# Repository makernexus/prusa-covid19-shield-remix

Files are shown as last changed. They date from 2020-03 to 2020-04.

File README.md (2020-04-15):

MakerNexus local modifications
------------------------------

At [MakerNexus], we're working on
[making as many face-shields as possible][covidshieldnexus] as possible;
They will be in dire demand very soon and we got requests of thousands of them.
MakerNexus is coordinating the contact with the local hospitals and
as well the effort of non-Members of the maker-space to 3D print. We
have enough shield material to laser-cut, but of course 3D printing is the
slow part of manufacturing.

Please check out the [project page] if you are in the San Francisco
Bay Area and want to help.

We are using the [Prusa-rc3] design, but needed some modifications requested
by the local healthcare community.

### Design goals

When reviewing, the local healthcare providers requested

   * Weight-reduce front-part if possible.
   * Move the shield pins up so that there is material behind the openings
     of the shield-punches
   * Larger radius of crevices to allow better sterilization access.

Moving up the shield-pin requires a little bit of support material, but it
is not a problem to generate the necessary STL file where the supports should
be and use that in the Prusa slicer as support modifier.

### Download

Choose what bests fits your circumstances. GCode is 'ready to go', 3mf allows
printer adjustments, *.stl allows to use in your own slicer.

You can just use the files below directly. If you want to work on the repo,
pull requests are welcome, but please discuss things first on slack.

### Release content

We are only printing the 'thin' shield version now (15mm vs. 20mm before).

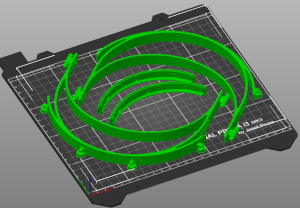
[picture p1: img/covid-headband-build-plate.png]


#### Cut to the chase: GCode ready to use

Recommended

  * For **PETG** [T9-PETG-Prusa.gcode](https://github.com/makernexus/prusa-covid19-shield-remix/raw/v1.9/fab/T9-PETG-Prusa.gcode) (right click, download or *save link as...*) GCode file placing 2 head-bands on build-plate. Ready to go on Prusa MK3(s) with 0.3mm layer, 100% infill, 240°C temp for PETG printing. This prints two thin bands which is faster to print and works fine with PETG.

  * For **PLA** [T9-PLA-Prusa.gcode](https://github.com/makernexus/prusa-covid19-shield-remix/raw/v1.9/fab/T9-PLA-Prusa.gcode) (right click, download or *save link as...*) Same for PLA. Currently this is the regular sized band as we still need to test if the thinner band will work with PLA.

The resulting headband has a version imprint on one temple with a letter
denoting `T` = thin band, and `s` = stacked, followed a version number.



#### More files

 * [thin_shield_with_support.stl](https://github.com/makernexus/prusa-covid19-shield-remix/raw/v1.9/fab/thin_shield_with_support.stl) and
   [thin_shield_no_support.stl](https://github.com/makernexus/prusa-covid19-shield-remix/raw/v1.9/fab/thin_shield_no_support.stl). The *with_support* version has already a support column included
   for printing the pin. Make sure you have **thin wall detection** enabled in
   your slicer. If you choose the *no support* version, you need
   to use your slicer to create support for the mounting pins.

If you have checked out code from github, you might need to first `make` it
and reload the STLs in the 3mf. The STLs and 3mf are usually only updated in
git for a new release (click on the stl in the list on the right in prusa slicer
and say 'reload from disk').

#### Stacked arrangement
There are 3mf's for stacks and makefile-rules to create various height stack
arrangements. The 3mf's with 'FAST' in their name are tweaked for very fast
prints, but it requires some tweaking depending on your filament to get the
flow-rate right and the separability correct. For details about the speed
improvements see the [Fast-Stacks](./Fast-Stacks.txt) documentation.

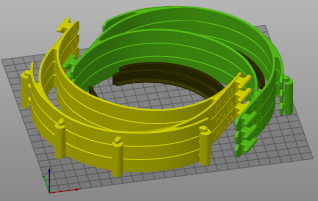
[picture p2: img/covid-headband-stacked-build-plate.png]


The way these stacks work is that they have a one-layer gap between them, with
the intent to have a weak layer adhesion there to be able to separate, but
still strong enough to print the next layers. This is the reason why it also
requires some tweaking which is very dependent on the printer and filament you
have, so we don't distribute any GCode. The gap height is 0.25mm, so this is
the layer thickness needed in your slicer (or modify the `print_layer_height`
in the Makefile).

If you use a different slicer than Prusa slicer, you can also create STLs for
the stacks and slice these.

```shell
make fab/thin-stack3.stl
```

### Faceshield

The face-shield has been optimized at MakerNexus to meet the needs of the
healthcare workers to be also protected above the headband. You find the
[maker-nexus-faceshield-cut.svg file](./baseline/maker-nexus-faceshield-cut.svg)
and [maker-nexus-faceshield-cut.dxf](./baseline/maker-nexus-faceshield-cut.dxf)
in the [baseline/](./baseline) subdirectory

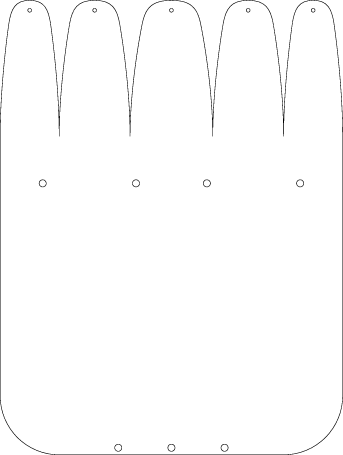
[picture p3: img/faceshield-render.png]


### Code

A simple OpenSCAD file that take the original STL and does the necessary
surgical changes.

### Slicer project file
A 3mf file is provided, so it can be loaded into slicer right away:

```
git clone https://github.com/hzeller/prusa-covid19-shield-remix.git
cd prusa-covid19-shield-remix
prusa-slicer thin_shield.3mf
```

### Replication Script

A script is provided that will take an existing Prusa Slicer project file (.3mf) with a single model already imported and fill the bed with as many of that model that will fit.  The script must be run with the python3 interpreter:

```
python3 scripts/replicate_model.py --help
usage: replicate_model.py [-h] [-w BED_WIDTH] [-d BED_DEPTH] -m MODEL -o
                          OUTPUT [--x_offset X_OFFSET] [--y_offset Y_OFFSET]
                          [--left_offset LEFT_OFFSET]
                          [--right_offset RIGHT_OFFSET]
                          [--front_offset FRONT_OFFSET]
                          [--rear_offset REAR_OFFSET] [-x X_SPACING]
                          [-X X_GAP] [-y Y_SPACING] [-Y Y_GAP]

optional arguments:
  -h, --help            show this help message and exit
  -w BED_WIDTH, --bed_width BED_WIDTH
                        Width of the print bed in mm (default: 250)
  -d BED_DEPTH, --bed_depth BED_DEPTH
                        Depth of the print bed in mm (default: 210)

required options:
  -m MODEL, --model MODEL
                        Baseline .3mf model file with one instance of the
                        model to be duplicated
  -o OUTPUT, --output OUTPUT
                        Output .3mf model file with one instance of the model
                        to be duplicated

keepout options:
  --x_offset X_OFFSET   X-axis offset from left and right edges of the bed
  --y_offset Y_OFFSET   Y-axis offset from front and rear edges of the bed
  --left_offset LEFT_OFFSET
                        Offset from the left side of the bed (x-axis, left
                        side only)
  --right_offset RIGHT_OFFSET
                        Offset from the right side of the bed (x-axis, right
                        side only)
  --front_offset FRONT_OFFSET
                        Offset from the front of the bed (y-axis, front only)
  --rear_offset REAR_OFFSET
                        Offset from the back of bed (y-axis, back only)

layout options:
  -x X_SPACING, --x_spacing X_SPACING
                        X-axis spacing in mm from the start of one instance of
                        the model to the next. This allows the models to
                        overlap in the X-axis.
  -X X_GAP, --x_gap X_GAP
                        X-axis gap from the edge of one model to the next
  -y Y_SPACING, --y_spacing Y_SPACING
                        Y-axis spacing in mm from the start of one instance of
                        the model to the next. This allows the models to
                        overlap in the Y-axis.
  -Y Y_GAP, --y_gap Y_GAP
                        Y-axis gap from the edge of one model to the next
```

There are only two required options (-m <source model> and -o <output model>).  The rest control the location on the bed / keepout areas where the objects can be laid out and then control the replication process itself.

All measurements are specified in mm and can be decimal values (e.g. 5.4).

The objects will be laid out in a grid pattern in rows and columns.  For the layout options, there are two ways the layout will be performed.  If the spacing options is specified, the object will be replicated at the given interval (e.g. every 10mm in the specified axis).  This allows each model to overlap the previous one.  If spacing is not provided, then the gap value will be used and the objects will have the specified gap between them.

With the specified bed dimensions, keepout area and layout options, the script will fit as many of the object as possible in the allowed area.

For the bottom support with the open curve facing downwards, it is desirable to have a gap in the X-axis, but to provide a spacing for the Y-axis.  The Makefile uses the following options to produce a dense, printable layout for the Prusa i3 mk3:

```
python3 scripts/replicate_model.py \
--model baseline/bottom_reinforcement-single-fast.3mf \
--output fab/bottom_reinforcement-full_plate-fast.3mf \
--x_offset 4 --front_offset 10 --x_gap 1 --y_spacing 8.2
```

With those options, the project file 'baseline/bottom\_reinforcement-single-fast.3ml' will be read and the first model replicated per the keepout/layout options.  It will then be written into the output project file 'fab/bottom\_reinforcement-full\_plate-fast.3mf'.

The default bed size (250 x 210) will be used with 4mm of space on the left and right side and 10mm of space on the bottom and 5mm on top.  (I have added more space to the bottom for the mk3 as the bottom corners aren't heated as well and the model may warp and get knocked off of the bed in those locations).  When laying out the replicated model, it will keep a 1mm gap between the columns and lay out the model vertically every 8.2mm.  That leaves enough gap between each so that the separate instances don't join together when printed.

This is what the output looks like:

```
python3 scripts/replicate_model.py --model baseline/bottom_reinforcement-single-fast.3mf --output fab/bottom_reinforcement-full_plate-fast.3mf --x_offset 4 --front_offset 10 --rear_offset 5 --x_gap 1 --y_spacing 8.2
replicate_model: Bed dimensions: [250 x 210]
replicate_model: Bed keep-out:
replicate_model:                 Rear: 5.0
replicate_model:           -----------------------
replicate_model:           |                     |
replicate_model: Left: 4.0 |                     | Right: 4.0
replicate_model:           |                     |
replicate_model:           -----------------------
replicate_model:                 Front: 10.0
replicate_model:
replicate_model: Processing project file (.3mf): baseline/bottom_reinforcement-single-fast.3mf
replicate_model: Model dimensions: [120.0572968 x 30.5739136]
replicate_model: Printing 42 objects [2 x 21]
replicate_model: Output project file (.3mf): fab/bottom_reinforcement-full_plate-fast.3mf
replicate_model: Complete.
```

### GCode
There is also gcode directly sliced for Prusa MK3(s). See above.

### Development

For building, use the Makefile to create all the artifacts from the *.scad
file

```
make
```

### License

License: [CC-BY-NC]

This is based on the Prusa design
https://www.prusaprinters.org/prints/25857-prusa-protective-face-shield-rc2

[MakerNexus]: https://www.makernexus.com/
[covidshieldnexus]: https://www.covidshieldnexus.org/
[prusa-rc3]: https://www.prusaprinters.org/prints/25857-prusa-protective-face-shield-rc3
[CC-BY-NC]: https://creativecommons.org/licenses/by-nc/4.0/
[project page]: http://makernexuswiki.com/index.php?title=3D_printed_face_shields
[prusa-slicer]: https://www.prusa3d.com/prusaslicer/

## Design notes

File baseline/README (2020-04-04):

All Licenses for these files: CC-BY-NC

The baseline STL we were starting out with.
https://www.prusaprinters.org/prints/25857-prusa-protective-face-shield-rc2

The RC2-nexusized files are made by Rich Rauenzahn, using a CAD model
provided by Adafruit This includes changes based on feedback from our
healthcare providers.

Adafruit tutorial: http://youtube.com/watch?v=BYPWB5-auQE

The maker-nexus-faceshield-cut.svg is the laser cutting instruction for the
faceshield. It has the MakerNexus improvements in coordination with the local
healthcare providers, protecting above the head.
maker-nexus-faceshield-cut.dxf is a DXF version of the same thing (it is
created by the Makefile one level up, but checked in here for convenience).

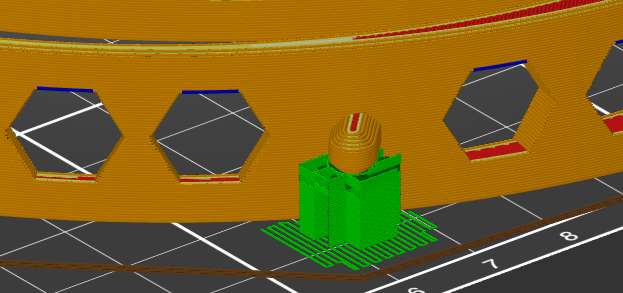
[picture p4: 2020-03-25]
img/minimal-support.png

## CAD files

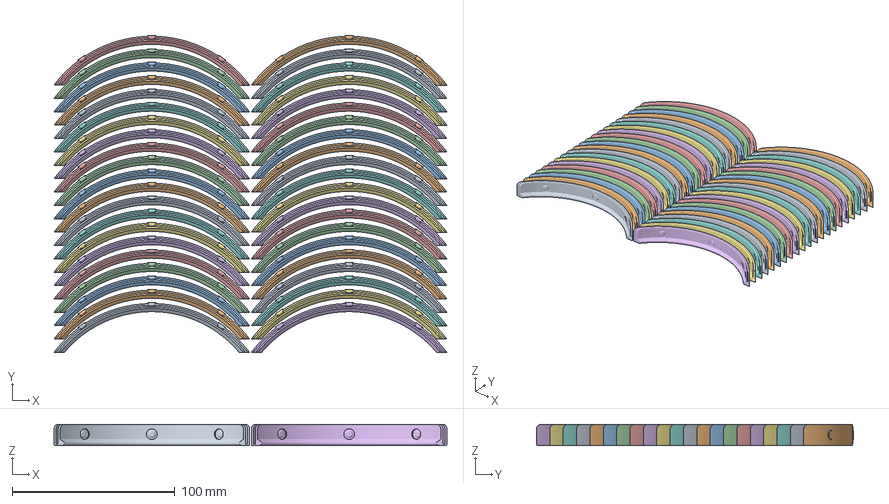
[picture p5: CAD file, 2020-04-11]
fab/bottom_reinforcement-full_plate-fast.3mf
241.1 x 194.6 x 13.0 mm

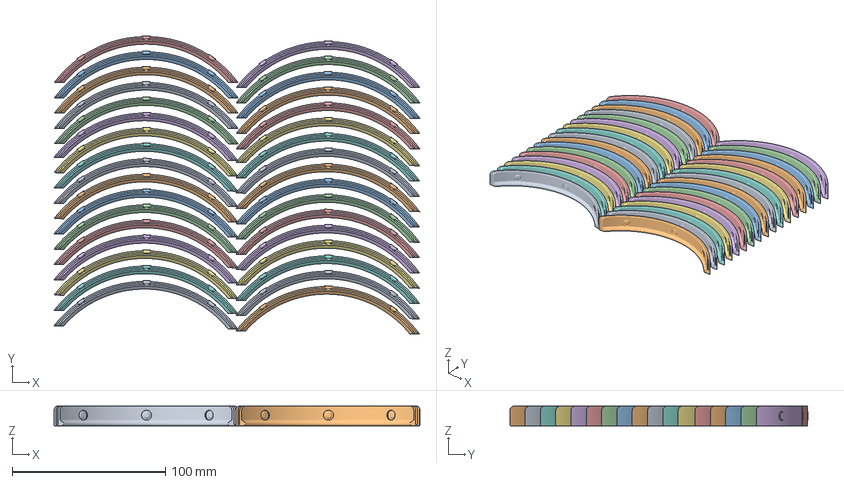
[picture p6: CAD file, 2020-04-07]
plate-full-of-bottom-supports.3mf
239.1 x 195.0 x 13.0 mm
bottom_reinforcement.stl x 2

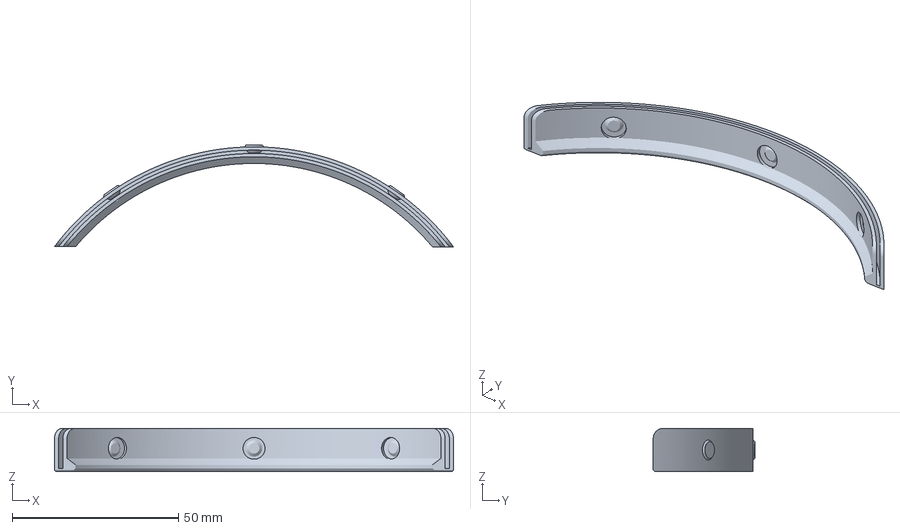
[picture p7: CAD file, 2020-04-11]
baseline/bottom_reinforcement-single-fast.3mf
120.1 x 30.6 x 13.0 mm

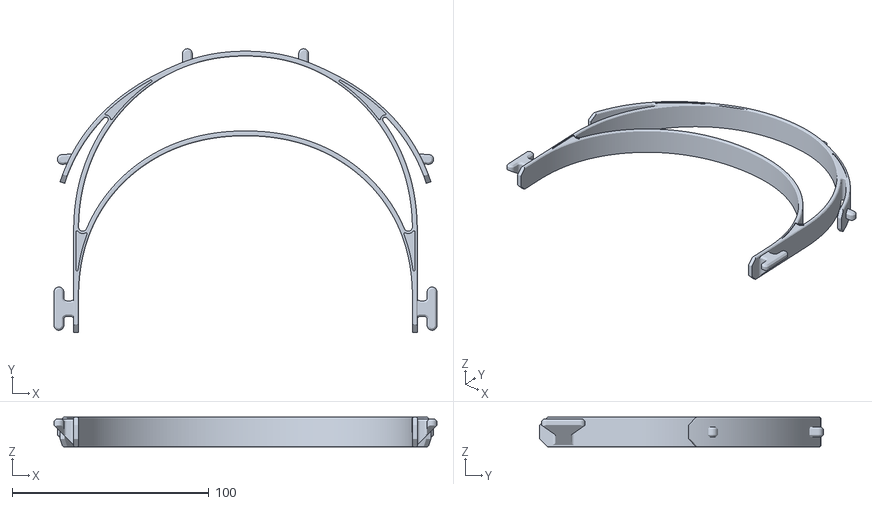
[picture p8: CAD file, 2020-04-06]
baseline/RC2-nexusized-thin-pla.stl
194.5 x 144.0 x 15.0

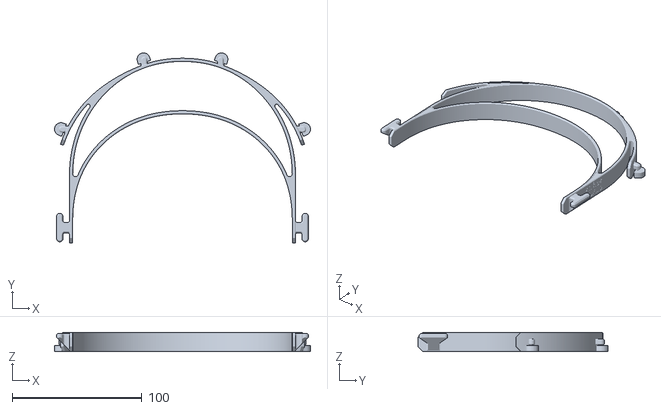
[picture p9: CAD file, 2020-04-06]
fab/thin_shield_with_support.stl
197.6 x 146.9 x 15.0

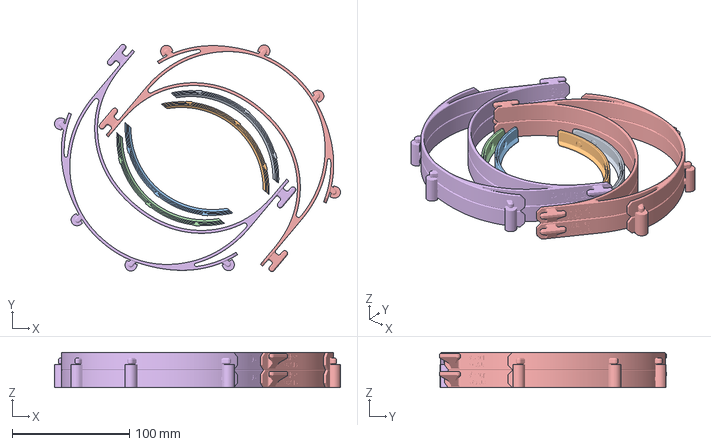
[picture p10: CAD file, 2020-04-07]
thin-shield-4stack_2x2-FAST.3mf
244.4 x 194.3 x 30.2 mm
bottom_reinforcement.stl
thin-stack2.stl

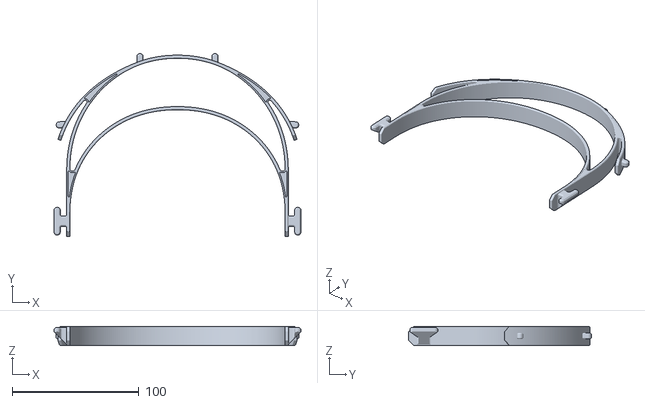
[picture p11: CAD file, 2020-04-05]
baseline/RC2-nexusized-thin.stl
194.5 x 144.0 x 15.0

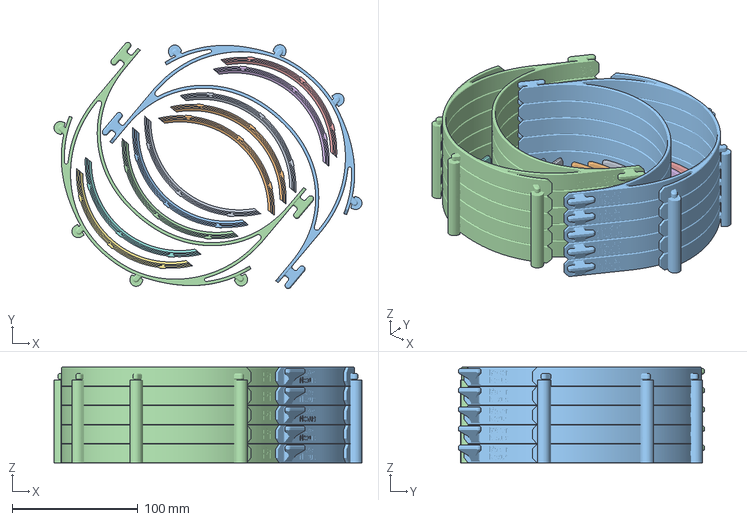
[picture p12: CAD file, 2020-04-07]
thin-shield-10stack_2x5-FAST.3mf
244.6 x 195.6 x 76.0 mm
bottom_reinforcement.stl
thin-stack5.stl

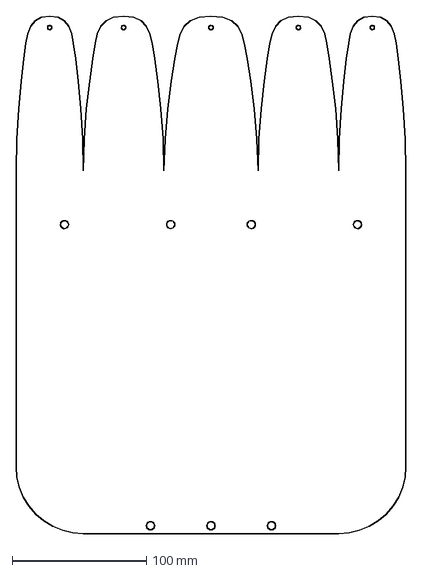
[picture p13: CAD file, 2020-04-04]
baseline/maker-nexus-faceshield-cut.dxf
290.0 x 385.0 mm

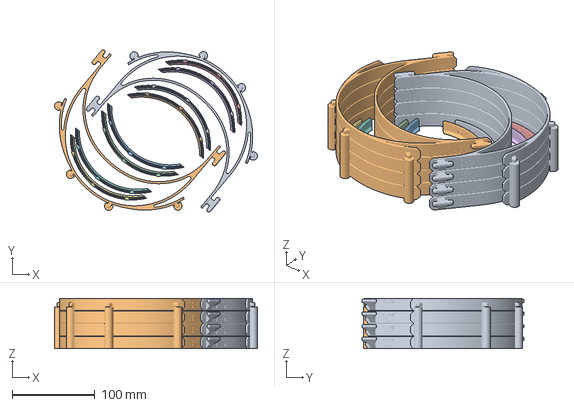
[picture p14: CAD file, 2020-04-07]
thin-shield-8stack_2x4-FAST.3mf
244.7 x 195.8 x 60.8 mm
bottom_reinforcement.stl
thin-stack4.stl

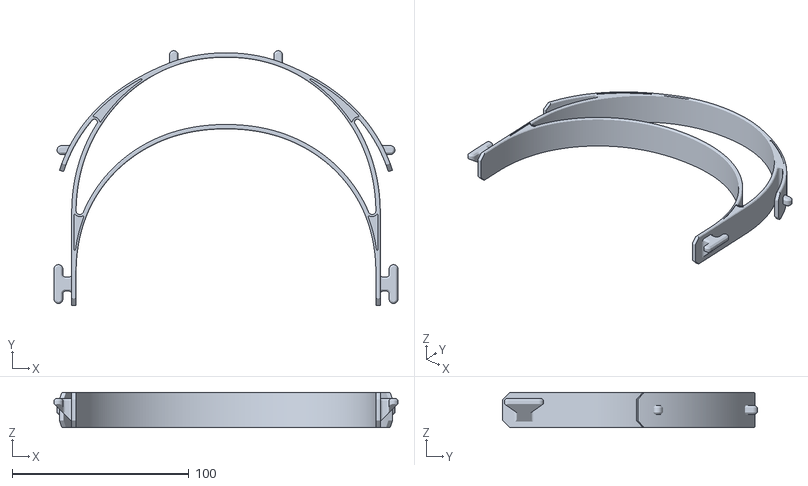
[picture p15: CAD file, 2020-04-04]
baseline/RC2-nexusized-normal.stl
194.5 x 144.0 x 20.0

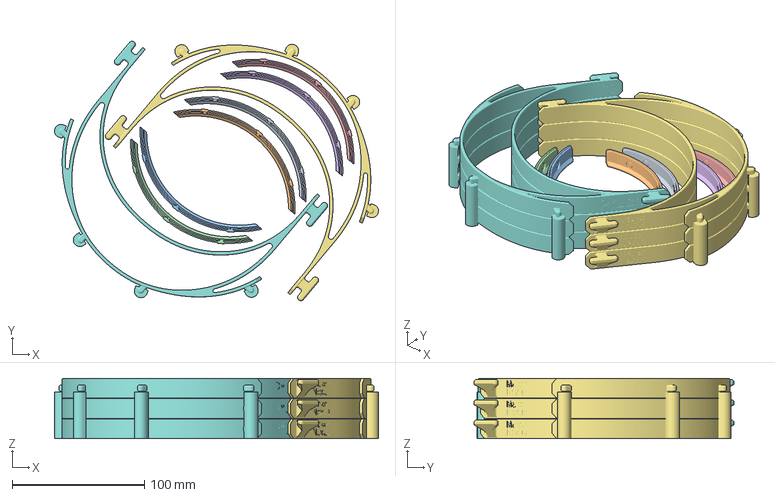
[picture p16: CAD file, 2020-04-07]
thin-shield-6stack_2x3-FAST.3mf
244.7 x 196.1 x 45.5 mm
bottom_reinforcement.stl
thin-stack3.stl

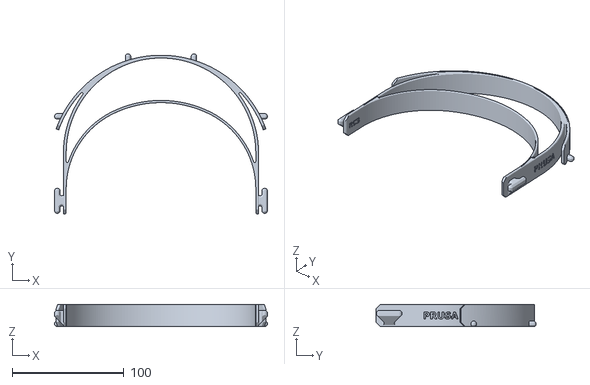
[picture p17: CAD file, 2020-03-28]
baseline/covid19_headband_rc3.stl
191.0 x 143.8 x 20.0

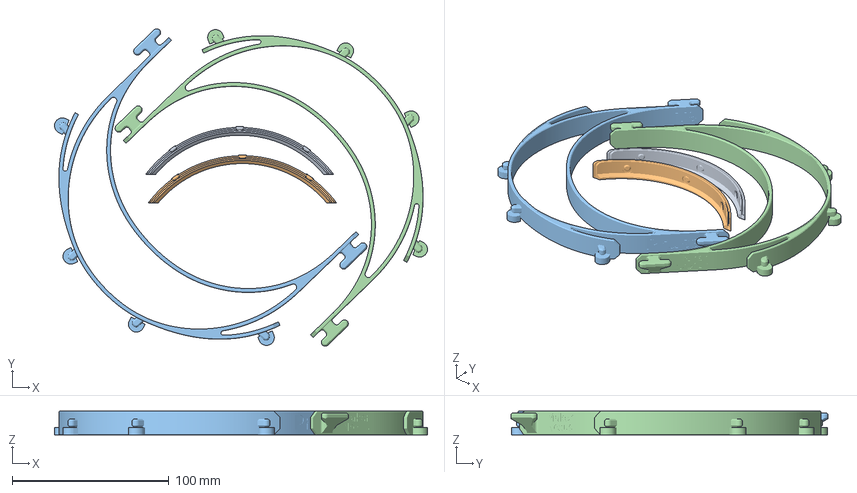
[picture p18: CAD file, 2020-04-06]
thin_shield.3mf
237.9 x 202.4 x 15.0 mm
bottom_reinforcement.stl
thin_shield_with_support.stl

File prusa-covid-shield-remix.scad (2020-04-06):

// -*- mode: scad; c-basic-offset: 2; indent-tabs-mode:nil -*-
// Incoroprating some feedback from local healthcare providers
//   * weight-reducing of front-part if possible.
//   * Move the shield buttons up so that there is material behind the openings
//     of the shield-punches

$fn=32;
e=0.01;

// Running version number. Should align with v1.x release.
// Intermediate git release WIP add a '
version_number="9";

support_column_foot_thickness=1.2;  // support-column: this much extra wide foot
support_wall=0.9;  // Should work without 'detect thin walls' in slicer.
support_column_radius=5.0;

pin_diameter=5;  // mm
print_layer_height=0.3;   // Layer thickness we're printing

// Experimental stacking.
default_stack_height = 3;
stack_separation=print_layer_height;

function get_band_thick() = 15;  // Always small these days

module maker_nexus_baseline_headband(version_text, is_pla=true) {
  is_thin = true;
  file = str("baseline/RC2-nexusized-", (is_pla ? "thin-pla":"thin"), ".stl");
  offset = -get_band_thick() / 2;
  text_depth=0.2;
  difference() {
    translate([0, 20, offset]) import(file, convexity=10);

    // Prusa Attribution
    translate([-87.2 + text_depth, -14, -5]) rotate([90, 0, -90])
      translate([0, 1, 0]) linear_extrude(height=2) text("Prusa", size=9, halign="center", font="style:Bold");

    // Maker Nexus Attribution
    translate([87.26 - text_depth, -30, 0]) {
      translate([0, 4, 1]) rotate([90, 0, 90]) linear_extrude(height=1)
        text("Maker", size=5, halign="left", font="style:Bold");
      translate([0, 4, -5]) rotate([90, 0, 90]) linear_extrude(height=1)
        text("Nexus", size=5, halign="left", font="style:Bold");
    }

    // Keep track of MakerNexus Version number
    translate([84.75 + text_depth, -48, -4]) rotate([90, 0, -90]) linear_extrude(height=1)
      text(str(version_text, version_number),
           size=8, halign="right", font="style:Bold");
  }
}

// Support for the pins.
module support_column(angle=0, dist=0, wall_thick=support_wall,
                      is_first=true, is_last=true, is_pla=false) {
  r=support_column_radius;
  // distances were originally calibrated for r=5mm
  dist=dist-(5-support_column_radius);
  band_thick = get_band_thick();
  level_thick=2*print_layer_height;
  support_platform = (get_band_thick() - pin_diameter)/2 - print_layer_height;
  h=is_last ? support_platform : band_thick + stack_separation;

  color("yellow") rotate([0, 0, angle]) translate([0, dist, -band_thick/2])
    rotate([0, 0, 180]) {
    intersection() {
      translate([-r, -r-2.5, 0]) cube([2*r, 2*r, h]);
      union() {
        difference() {
          union() {
            cylinder(r=r, h=h);  // Column
            translate([-r, 0, 0]) cube([2*r, 0.5*r, h]); // .. flattened
          }
          translate([0, 0, -e]) union() {  // Remove inside
            translate([0, 0, 0]) cylinder(r=r-wall_thick, h=h+2*e);
            translate([-(r-wall_thick), 0, 0]) cube([2*(r-wall_thick), r, h+2*e]);
          }
        }

        // The 'shelf' part.
        translate([0, -0.5, support_platform-level_thick]) {
          translate([-r, 0, 0]) cube([2*r, 3, level_thick]);
          cylinder(r=r-wall_thick, h=level_thick);
        }

        // shelf supports
        support_edge_length = (r/2);
        translate([0, 0, support_platform-level_thick]) rotate([-90, 0, 0]) {
          translate([-(r-wall_thick), 0, 0])  {
            linear_extrude(height=r) polygon([[0, 0], [support_edge_length, 0], [0, support_edge_length]]);
          }
          translate([r-wall_thick, 0, 0]) {
            linear_extrude(height=r) polygon([[0, 0], [-support_edge_length, 0], [0, support_edge_length]]);
          }
          rotate([90, 0, 0]) translate([0, 0, -support_edge_length]){
            rotate_extrude(angle=180) translate([-(r-wall_thick), 0, 0]) polygon([[0, 0], [support_edge_length, support_edge_length], [0, support_edge_length]]);
          }
        }
        translate([-((r/2)+.5), 1, support_platform-(level_thick*2)]) cube([r+.5, 3, level_thick]);
      }
    }

    // Some stability foot if we're first. Don't make it entirely solid, as
    // that seems to be too well connected to the build-bed.
    if (is_first) intersection() {
      translate([-15/2, -7.5, 0]) cube([15, 10, 1]);
      union() {
        difference() {
          cylinder(r=r, h=.3);
          translate([0, 0, -e]) cylinder(r=r-support_column_foot_thickness-wall_thick, h=0.3+2*e);
        }
        translate([-r, 1, 0]) cube([2*r, 1.5, 0.3]);
      }
    }
  }
}

// The angle and distance the pins. We only need some rough position,
// as we just use this as a cut-out where we do the material-move operation.
// There we just move the bottom part up and replace the bottom part with
// what we found above (angles, positions determined empirically)
pin_angle_distances = [ [18.5, 94.8], [-18.5, 94.8], [69, 100.5], [-69, 100.5]];

module print_shield(version_text, do_punches=false, pin_support=false,
                    is_pla=false, is_first=true, is_last=true) {
  maker_nexus_baseline_headband(version_text, is_pla);
  // Add support for the pins.
  if (pin_support) {
    for (x = pin_angle_distances) support_column(x[0], x[1],
                                                 is_pla=is_pla,
                                                 is_last=is_last,
                                                 is_first=is_first);
  }
}

// Print a stack of face-shields.
module print_stack(count=default_stack_height, is_pla=false) {
  stack_distance = get_band_thick() + stack_separation;
  base_version = is_pla ? "s" : "S";
  for (i = [0:1:count-e]) {
    translate([0, 0, i*stack_distance]) {
      is_first = (i == 0);
      is_last = (i == (count - 1));
      print_shield(base_version, pin_support=true,
                   is_first=is_first, is_last=is_last,
                   is_pla=is_pla);
    }
  }
}


/* Some functions which we use to generate named
 * STLs directly in the Makefile
 */
module thin_shield_no_support() {
  print_shield("T", pin_support=false, is_pla=false);
}
module thin_shield_with_support() {
  print_shield("T", pin_support=true, is_pla=false);
}

module thin_pla_shield_no_support() {
  print_shield("t", pin_support=false, is_pla=true);
}
module thin_pla_shield_with_support() {
  print_shield("t", pin_support=true, is_pla=true);
}

module thin_stack_with_support() {
  print_stack(default_stack_height, is_pla=false);
}

// Local testing call. Can be left in, it will be ignored in the Makefile.
thin_pla_shield_with_support();
//print_stack(3, is_thin=true);

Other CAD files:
fab/thin_shield_no_support.stl
fab/thin_pla_shield_with_support.stl
fab/bottom_reinforcement.stl
baseline/covid19_headband_rc2.stl
cad/prusa-faceshield-with-MakerNexus-mods.f3z
thin_pla_shield.3mf

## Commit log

2020-03-25 Don't punch holes where we need the stability for holding the shield.
    [covid19_headband_rc2.stl, prusa-covid-shield-remix.scad]
2020-03-25 Add generated stl. github has a way to display that.
    [prusa-covid-shield-remix.stl]
2020-03-25 move the pins up.
    [prusa-covid-shield-remix.scad, prusa-covid-shield-remix.stl]
2020-03-25 Add support modifier.
    [prusa-covid-shield-remix-print_shield.stl, prusa-covid-shield-remix-support_modifier.stl, prusa-covid-shield-remix.scad, prusa-covid-shield-remix.stl]
2020-03-25 Use supports and save as 3mf
    [bottom_reinforcement.stl, prusa-covid-shield-remix-print_shield.stl, prusa-covid-shield-remix-support_modifier.stl, prusa-covid-shield-remix.3mf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]
2020-03-25 Update comments.
    [prusa-covid-shield-remix.scad]
2020-03-25 Move original files to baseline/; harmonize indentation in *.scad
    [bottom_reinforcement.stl, covid19_headband_rc2.stl, prusa-covid-shield-remix.scad]
2020-03-25 Simplify: instead of moving things down, replace bottom part with symmetric copy from top.
    This way, we also capture the taper and champfer.
    [prusa-covid-shield-remix.scad]
2020-03-25 Update stl and 3mf.
    [prusa-covid-shield-remix-print_shield.stl, prusa-covid-shield-remix.3mf]
2020-03-25 Fix comment indentation.
    [prusa-covid-shield-remix.scad]
2020-03-25 Use some overlap to prevent possiblity of broken manifolds.
    Not an actual issue, but can't harm to be careful.
    [prusa-covid-shield-remix-print_shield.stl, prusa-covid-shield-remix.scad]
2020-03-26 Update to print with 3 shells.
    [prusa-covid-shield-remix.3mf]
2020-03-26 Include version emboss for next iteration.
    [prusa-covid-shield-remix.scad]
2020-03-26 Qualify version.
    [prusa-covid-shield-remix.scad]
2020-03-27 Use STL-included supports that are easier to break off.
    [prusa-covid-shield-remix-print_shield.stl, prusa-covid-shield-remix-support_modifier.stl, prusa-covid-shield-remix.3mf, prusa-covid-shield-remix.scad]
2020-03-28 Baseline RC3; add configuration options o add hexagonal holes (but upright punch). o provide a 'shorter' version with centered pins.
    [prusa-covid-shield-remix.scad]
2020-03-28 Add makefile support to generate short and normal shield.
    [covid19_headband_rc3.stl, prusa-covid-shield-remix.scad, short_shield.3mf, short_shield_no_support.stl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]
2020-03-28 Add normal shield stl and 3mf
    [normal_shield.3mf, normal_shield_no_support.stl, normal_shield_with_support.stl]
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2020-03-28 Remove one hole on the outer edge right and left.
    [normal_shield.3mf, normal_shield_no_support.stl, normal_shield_with_support.stl, prusa-covid-shield-remix.scad]
2020-03-28 Make hex-holes horizontal again.
    [normal_shield.3mf, normal_shield_no_support.stl, normal_shield_with_support.stl, prusa-covid-shield-remix.scad]
2020-03-28 Use 100% infill. Make supports a little larger.
    [normal_shield.3mf, normal_shield_no_support.stl, normal_shield_with_support.stl, prusa-covid-shield-remix.scad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]
2020-03-28 Some cleanup: remove older versions of gcode.
    [prusa-covid-shield-remix-print_shield.stl, prusa-covid-shield-remix-support_modifier.stl, prusa-covid-shield-remix.3mf]
2020-03-28 Make the support column with a foot to better adhere to bed.
    [normal_shield.3mf, normal_shield_no_support.stl, normal_shield_with_support.stl, prusa-covid-shield-remix.scad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]
2020-03-28 Don't include short_shield yet as final files until they are tested.
    [short_shield_no_support.stl, short_shield_with_support.stl]
2020-03-29 Add experimental stack support.
    [prusa-covid-shield-remix.scad]
2020-03-29 Rename 'short' to 'thin' for more clarity.
    [prusa-covid-shield-remix.scad, short_shield.3mf, thin_shield.3mf]
2020-03-29 Take version number from one central place.
    [prusa-covid-shield-remix.scad]
2020-03-29 Make the support column foot not quite as strongly adhering.
    It was very hard to remove from my built-plate, so making something
    in-between is proably better.
    (this is part of issue #1)
    [prusa-covid-shield-remix.scad]
2020-03-29 Add experimental stack separation layer support.
    [prusa-covid-shield-remix.scad]
2020-03-29 Add fab/*.scad,*.deps to .gitignore; Fixup README.md for new paths; Copy existing files into fab/ so README.md links work.
    [normal_shield.3mf, normal_shield_no_support.stl, normal_shield_with_support.stl]
2020-03-29 Makefile: point to fab/ targets; fab/: don't need 3mf
    [normal_shield.3mf]
2020-03-29 Remove old versions of stl and gcode before fab.
    [normal_shield_no_support.stl, normal_shield_with_support.stl]
2020-03-29 Prepare easier relases.
    * since prusa-slicer currently does not support relative paths
    of stl files to 3mf, we have to symbolic link these.
    * add experimental gcode creation, however the output is entirely
    different than triggered from the UI. Not using that yet.
    [prusa-covid-shield-remix.scad]
2020-03-29 Name version with a letter N not hex-symbol. Make support foot less aggressive stick.
    [prusa-covid-shield-remix.scad]
2020-03-29 Make base-foot configurable.
    [prusa-covid-shield-remix.scad]
2020-03-29 Centralize the place where we define what 'thin' means.
    [prusa-covid-shield-remix.scad]
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2020-03-29 Parameterize some supports, thin them out. Make more and taller. (#3)
    * Windows saves .scad with crlf -- fix that at checkin
    * Make support constants globals, reduce cylinder size, more perforation supports, taller perforation supports, thinner support walls
    [prusa-covid-shield-remix.scad]
2020-03-29 re-arrange some variables and tweak values.
    [prusa-covid-shield-remix.scad]
2020-03-29 Update 3mf to detect thin walls.
    [normal_shield.3mf, thin_shield.3mf]
2020-03-29 Fix offset for supports to be dependent on thin state. (#4)
    [prusa-covid-shield-remix.scad]
2020-03-29 Cut out the right part for the support.
    [prusa-covid-shield-remix.scad]
2020-03-29 Make the support column height based on how thin is thin.
    [prusa-covid-shield-remix.scad]
2020-03-29 Make print-layer height a configurable value.
    [prusa-covid-shield-remix.scad]
2020-03-30 No holes on thin or normal band.
    [prusa-covid-shield-remix.scad]
2020-03-30 Preparing new STLs for v4
    [normal_shield_with_support.stl, thin_shield_with_support.stl]
2020-03-30 Update 3mf and pre-gen gcode.
    [normal_shield.3mf, thin_shield.3mf]
2020-03-30 Stack: make layer separation distance depending on layer support.
    [normal_shield_no_support.stl, prusa-covid-shield-remix.scad]
2020-03-30 Fast stacks (#5)
    * Add fast .3mf for 2 quad-stacks based on Prusa's .3mf for RC3.1
    * Added Fast-Stacks.txt with a description of the mods && configuration for fast printing
    [thin-shield-8stack[2x4]-FAST.3mf]
2020-03-30 Use provide_stack_separation_support=false by default.
    [prusa-covid-shield-remix.scad]
2020-03-30 Don't use funny unicode characters in stack version.
    [prusa-covid-shield-remix.scad]
2020-03-30 Create makefile rules to output various stack STLs.
    make fab/thin-stack3.stl
    makes a stack of height 3.
    make stacks
    will make all of them and links them in the toplevel directory, which
    is a requirement for 'reload from disk' to work in prusa-slicer.
    [prusa-covid-shield-remix.scad]
2020-03-30 More fast stacks (#8)
    * Reoriented model on the bed to allow space for a skirt
    * Added .3mf files for dual 2, 3 and 5 model stacks
    * Disabled two support pieces that were inadvertently enabled.`
    [thin-shield-10stack[2x5]-FAST.3mf, thin-shield-4stack[2x2]-FAST.3mf, thin-shield-6stack[2x3]-FAST.3mf, thin-shield-8stack[2x4]-FAST.3mf]
2020-03-30 Updated stack models (#9)
    * Added thin-stack2.stl
    * Renamed stack 3mf files.
    * Updated to latest model with unique code for stacks.
    [thin-shield-10stack[2x5]-FAST.3mf, thin-shield-10stack_2x5-FAST.3mf, thin-shield-4stack[2x2]-FAST.3mf, thin-shield-4stack_2x2-FAST.3mf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]
2020-03-30 Add larger fillets for easier sanitization liquid access.
    [prusa-covid-shield-remix.scad]
2020-03-30 Fixed purge line in printer profile (#10)
    [thin-shield-10stack_2x5-FAST.3mf, thin-shield-4stack_2x2-FAST.3mf, thin-shield-6stack_2x3-FAST.3mf, thin-shield-8stack_2x4-FAST.3mf]
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2020-04-11 Replicate script 2 (#27)
    * Added new script to fill a build plate with instances of a single model
    * Fixed issue with 3dmodel xml
    * Added build step to create a full plate of fast-printing bottom reinforcement pieces for mk3.
    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
    [bottom_reinforcement-full_plate-fast.3mf, bottom_reinforcement-single-fast.3mf]
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
